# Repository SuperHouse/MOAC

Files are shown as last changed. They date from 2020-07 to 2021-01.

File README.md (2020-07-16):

Mini Open Adaptive Controller
==============================

Universal input device that allows external switches, buttons, etc
to be connected using 3.5mm mono plugs, and then emulate a USB
keyboard, mouse, joystick, or game controller to send HID events
to a computer or game console.

This allows custom-made assistive-technology input devices to be
connected to a computer or game console. Functionally this is very
similar to the Microsoft Xbox Adaptive Controller, but with fewer
inputs, a fully open-source design, a display, and more device emulation
options.

Based on the ATmega32u4 microcontroller, compatible with the Arduino
Leonardo.

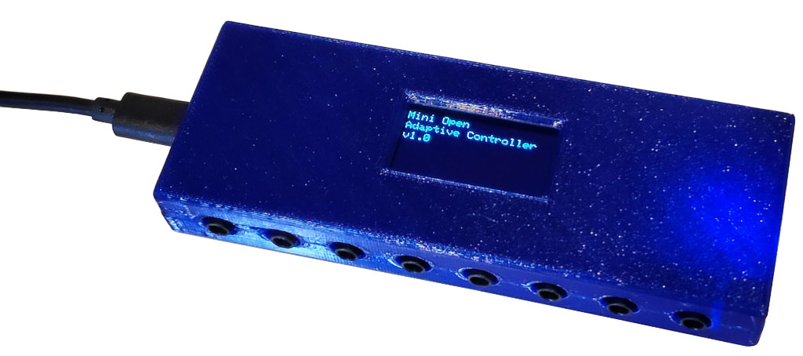
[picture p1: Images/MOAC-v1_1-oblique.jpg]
Mini Open Adaptive Controller


Features:

 * 8 switch inputs with 3.5mm mono sockets
 * USB-C socket for connection to computer, game controller, etc
 * Customise the software to suit your needs
 * 128x64 OLED module (SH1106)
 * ATmega 32u4 MCU (Arduino compatible)
 * Piezo beeper
 * Beep on/off switch
 * HWB (hardware boot) button and solder jumper to allow disabling bootloader

You can view more details at:

  http://www.superhouse.tv/moac

Hardware
--------
The "Hardware" directory contains the PCB design as an EAGLE project.
EAGLE PCB design software is available from Autodesk free for
non-commercial use.

Firmware
--------
The "Firmware" directory contains multiple versions. We have experimented
with different OLEDs and libraries during development, so this is a
collection of the different firmware versions.

The most recent hardware uses a 128x64 OLED with the SH1106 driver.

Unfortunately the various SH1106 drivers are a bit strange, and the best
I've found is the version of Adafruit's SSD1306 library that was forked
by wonho-maker and modified to add SSD1306 support. That version is not
available through the Arduino library manager, so it's been embedded
directly within the project.

Enclosure
---------
The "Enclosure" directory contains STLs for a case that can be
3D-printed.

The two halves of the case should be printed with the flat face down to
the printer bed.

The case can be held shut by countersunk self-tapping screws.

Credits
-------
 * Jonathan Oxer <jon@oxer.com.au>
 * Chris Fryer <chris.fryer78@gmail.com>

License
-------
Copyright 2018-2020 SuperHouse Automation Pty Ltd  www.superhouse.tv  

The hardware portion of this project is licensed under the TAPR Open
Hardware License (www.tapr.org/OHL). The "license" folder within this
repository contains a copy of this license in plain text format.

The software portion of this project is licensed under the Simplified
BSD License. The "licence" folder within this project contains a
copy of this license in plain text format.

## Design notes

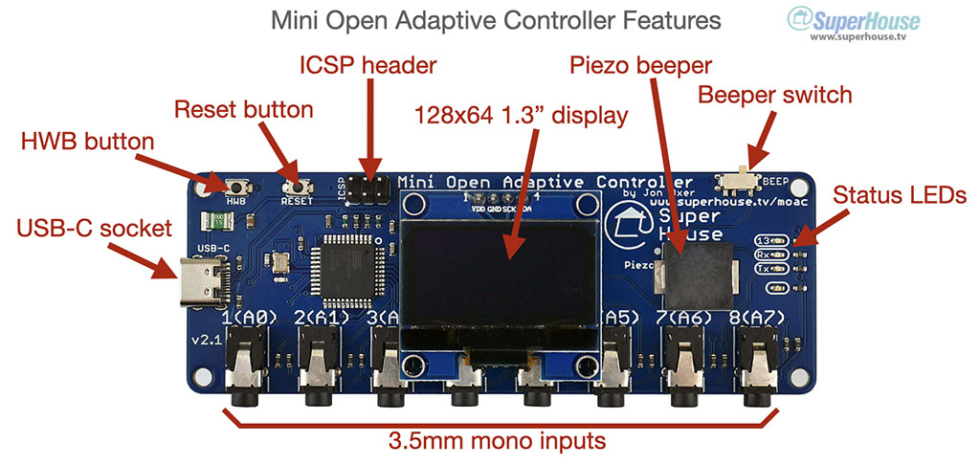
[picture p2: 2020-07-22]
Images/MOAC-v2_1-features.jpg

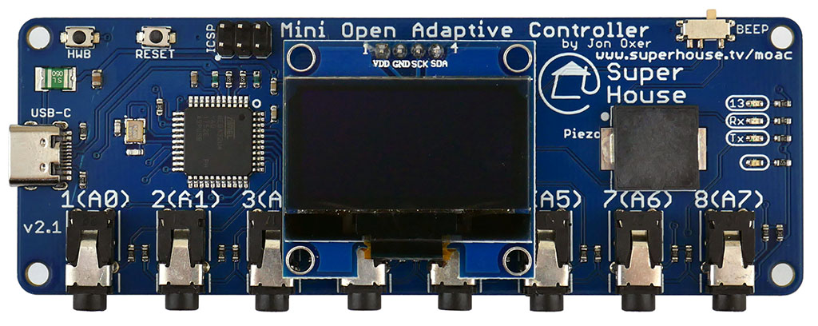
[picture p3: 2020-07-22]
Images/MOAC-v2_1-top.jpg

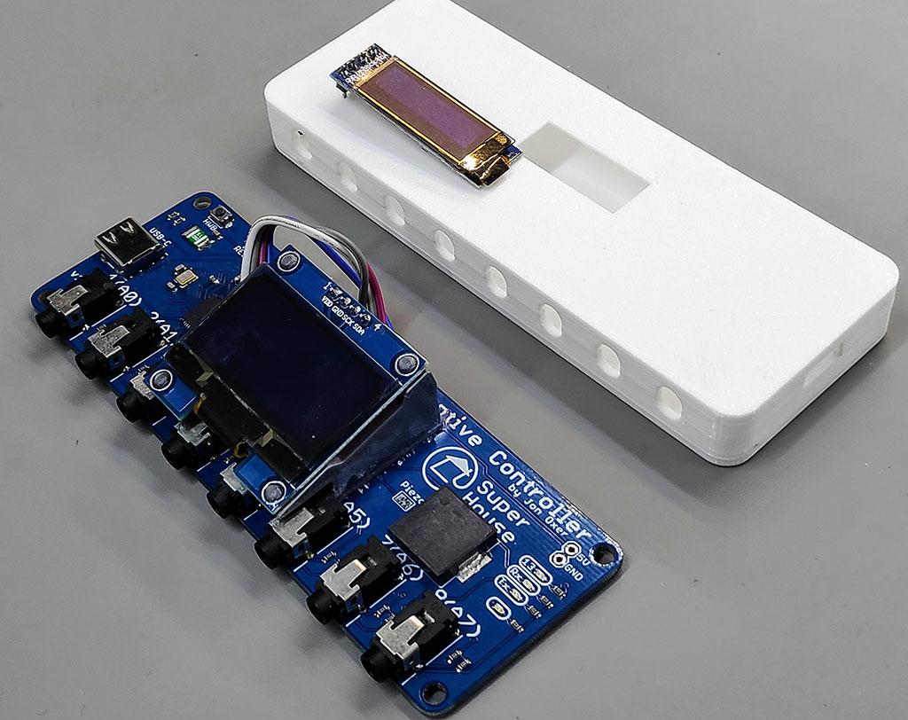
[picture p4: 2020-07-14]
Images/MOAC-v1_0-screen-size.jpg

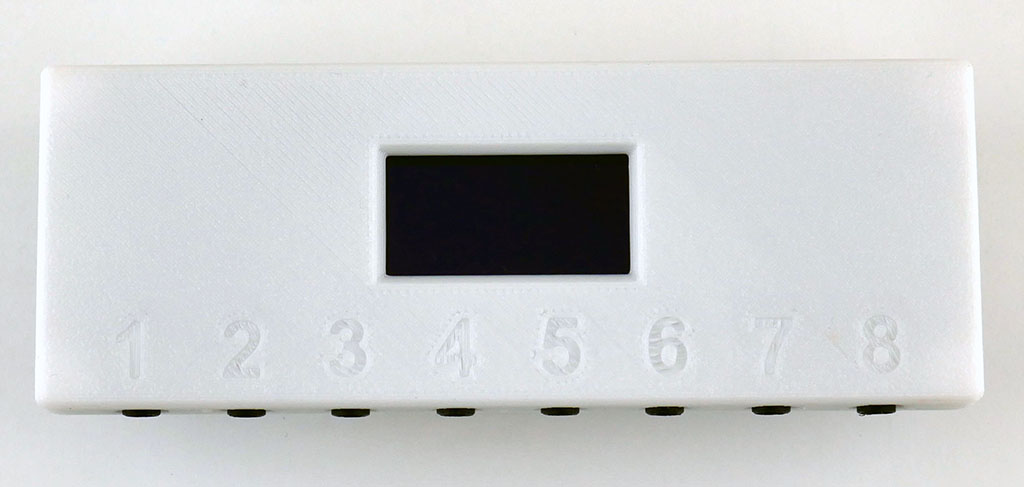
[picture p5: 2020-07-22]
Images/MOAC-v2_1-case-front.jpg

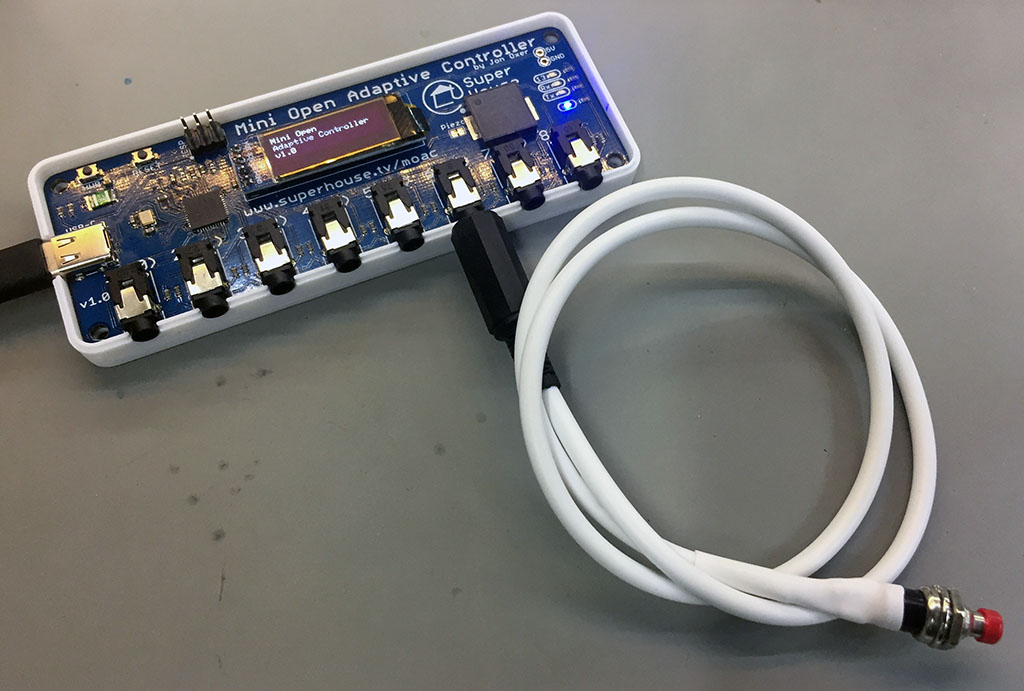
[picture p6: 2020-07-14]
Images/MOAC-v1_0-prototype-1-raw.jpg

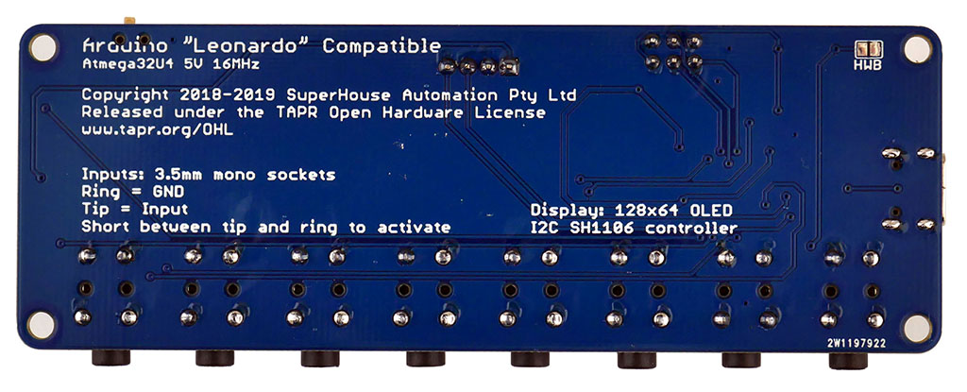
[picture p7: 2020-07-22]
Images/MOAC-v2_1-bottom.jpg

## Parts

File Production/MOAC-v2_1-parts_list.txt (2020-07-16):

Partlist

Exported from MOAC.sch at 16/7/20 12:54 PM

EAGLE Version 9.6.2 Copyright (c) 1988-2020 Autodesk, Inc.

Assembly variant: 

Part     Value                   Device                  Package              Library                 Sheet

C1       100nF                   CAP0603                 C0603                SuperHouse-DiscreteSemi 1
C2       100nF                   CAP0603                 C0603                SuperHouse-DiscreteSemi 1
C3       10uF                    CAP0805                 C0805                SuperHouse-DiscreteSemi 1
C4       1uF                     CAP0603                 C0603                SuperHouse-DiscreteSemi 1
C5       15pF                    CAP0603                 C0603                SuperHouse-DiscreteSemi 1
C6       15pF                    CAP0603                 C0603                SuperHouse-DiscreteSemi 1
F1       500mA PTC 1812          PTC050                  1812                 SuperHouse-Fuses        1
IC1      ATMEGA32U4NT-TQFP       ATMEGA32U4NT-TQFP       TQFP44               SuperHouse-MCUs         1
ICSP     ICSP                    ICSPPTH                 2X03PTH              SuperHouse-Connectors   1
J1       3.5mm                   AUDIO-JACK-PJ321        AUDIO-JACK-PJ321     SuperHouse-Connectors   1
J2       3.5mm                   AUDIO-JACK-PJ321        AUDIO-JACK-PJ321     SuperHouse-Connectors   1
J3       3.5mm                   AUDIO-JACK-PJ321        AUDIO-JACK-PJ321     SuperHouse-Connectors   1
J4       3.5mm                   AUDIO-JACK-PJ321        AUDIO-JACK-PJ321     SuperHouse-Connectors   1
J5       3.5mm                   AUDIO-JACK-PJ321        AUDIO-JACK-PJ321     SuperHouse-Connectors   1
J6       3.5mm                   AUDIO-JACK-PJ321        AUDIO-JACK-PJ321     SuperHouse-Connectors   1
J7       3.5mm                   AUDIO-JACK-PJ321        AUDIO-JACK-PJ321     SuperHouse-Connectors   1
J8       3.5mm                   AUDIO-JACK-PJ321        AUDIO-JACK-PJ321     SuperHouse-Connectors   1
J10      USB-C-16P-16P           USB-C-16P-16P           USB-C-16P            SuperHouse-Connectors   1
LED1     BLUE                    LED0603                 LED-0603             SuperHouse-LEDs         1
LED2     RED                     LED0603                 LED-0603             SuperHouse-LEDs         1
LED3     GREEN                   LED0603                 LED-0603             SuperHouse-LEDs         1
LED4     RED                     LED0603                 LED-0603             SuperHouse-LEDs         1
MOD2     OLED-I2C128X64-1.3-5.08 OLED-I2C128X64-1.3-5.08 OLED-128X64-1.3-5.08 SuperHouse-Displays     1
PIEZO    BUZZERSMD12X12          BUZZERSMD12X12          BUZZER-12X12-SMT     SuperHouse-Audio        1
R1       22R                     RESISTOR0603            R0603                SuperHouse-DiscreteSemi 1
R2       10K                     RESISTOR0603            R0603                SuperHouse-DiscreteSemi 1
R3       4K7                     RESISTOR0603            R0603                SuperHouse-DiscreteSemi 1
R4       1K                      RESISTOR0603            R0603                SuperHouse-DiscreteSemi 1
R5       1K                      RESISTOR0603            R0603                SuperHouse-DiscreteSemi 1
R6       22R                     RESISTOR0603            R0603                SuperHouse-DiscreteSemi 1
R7       5.1K                    RESISTOR0603            R0603                SuperHouse-DiscreteSemi 1
R8       1K                      RESISTOR0603            R0603                SuperHouse-DiscreteSemi 1
R9       1K                      RESISTOR0603            R0603                SuperHouse-DiscreteSemi 1
R10      1K                      RESISTOR0603            R0603                SuperHouse-DiscreteSemi 1
R11      1K                      RESISTOR0603            R0603                SuperHouse-DiscreteSemi 1
R12      1K                      RESISTOR0603            R0603                SuperHouse-DiscreteSemi 1
R13      10K                     RESISTOR0603            R0603                SuperHouse-DiscreteSemi 1
R14      10K                     RESISTOR0603            R0603                SuperHouse-DiscreteSemi 1
R15      10K                     RESISTOR0603            R0603                SuperHouse-DiscreteSemi 1
R16      10K                     RESISTOR0603            R0603                SuperHouse-DiscreteSemi 1
R17      1K                      RESISTOR0603            R0603                SuperHouse-DiscreteSemi 1
R18      5.1K                    RESISTOR0603            R0603                SuperHouse-DiscreteSemi 1
R19      1K                      RESISTOR0603            R0603                SuperHouse-DiscreteSemi 1
R20      1K                      RESISTOR0603            R0603                SuperHouse-DiscreteSemi 1
R21      1K                      RESISTOR0603            R0603                SuperHouse-DiscreteSemi 1
R22      10K                     RESISTOR0603            R0603                SuperHouse-DiscreteSemi 1
R23      10K                     RESISTOR0603            R0603                SuperHouse-DiscreteSemi 1
R24      10K                     RESISTOR0603            R0603                SuperHouse-DiscreteSemi 1
R25      10K                     RESISTOR0603            R0603                SuperHouse-DiscreteSemi 1
S9       RESET                   TAC_SWITCH_2PINSMT      TACTILE_SMD_3X4X2    SuperHouse-Switches     1
S10      HWB                     TAC_SWITCH_2PINSMT      TACTILE_SMD_3X4X2    SuperHouse-Switches     1
SJ1      HWB                     SJ-NORMAL               SJ                   SuperHouse-Jumpers      1
SW1      SWITCH-SPDT-4TABSSMT    SWITCH-SPDT-4TABSSMT    MK-12C02             SuperHouse-Switches     1
XTL1     16MHz                   CRYSTAL-GND3X2          CRYSTAL-SMD-3X2      SuperHouse-Oscillators  1
Z1       PGB1010603              TVS0603                 TVS0603              SuperHouse-DiscreteSemi 1
Z2       PGB1010603              TVS0603                 TVS0603              SuperHouse-DiscreteSemi 1

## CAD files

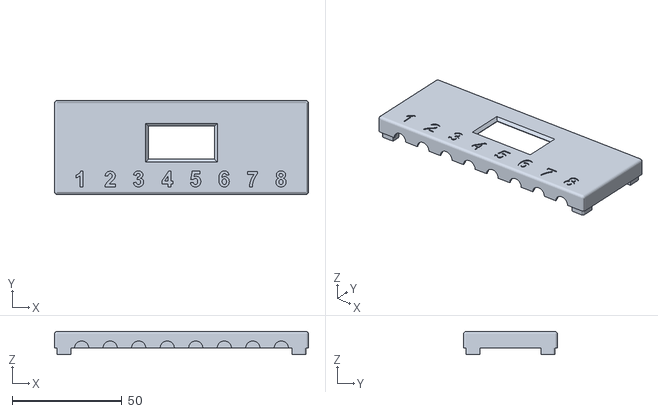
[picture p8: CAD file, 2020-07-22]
Enclosure/MOAC-case-top-v17.stl
115.8 x 42.8 x 10.6

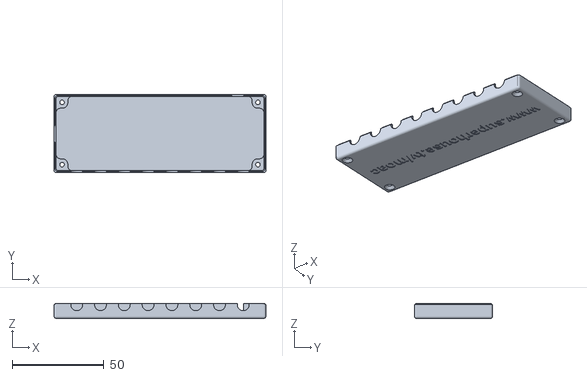
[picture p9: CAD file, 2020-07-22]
Enclosure/MOAC-case-bottom-v17.stl
115.8 x 42.8 x 8.10

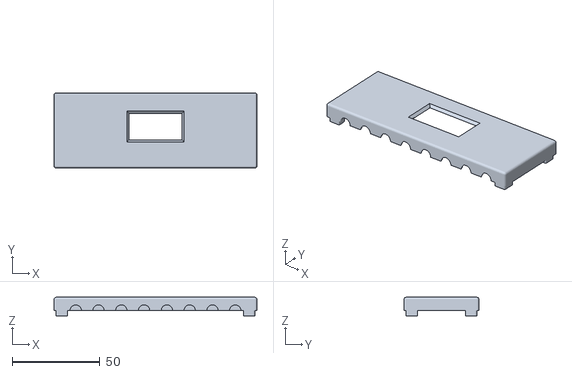
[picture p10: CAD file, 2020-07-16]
Enclosure/MOAC-case-top-v14.stl
115.8 x 42.8 x 10.6

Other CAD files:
Production/MOAC-tcream-v2_1.dxf
Enclosure/MOAC-case-top-v16.stl
Enclosure/MOAC-case-bottom-v16.stl
Enclosure/MOAC-case-bottom-v14.stl

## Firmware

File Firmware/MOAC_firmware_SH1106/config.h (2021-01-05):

/* ----------------- General config -------------------------------- */
// Messages generated by the inputs
char *g_macro_messages[] = {
  "a",       // 1: letter "a"
  "b\n",     // 2: letter "b" then start a new line
  "Hi ",     // 3: word "Hi" then a space
  "there\n", // 4: word "there" then start a new line
  "5",       // 5: number "5"
  "6",       // 6: number "6"
  "warp",    // Special "mouse warp" command
  "For more info, see: https://www.superhouse.tv/moac \n"  // 8: Print a help message!
};

// Mouse warp locations. Any input can be defined as a "warp" button, which
// will cause the mouse cursor to jump to each of the coordinates in turn.
// Warp locations are X/Y values, starting at 0,0 in the top left corner of
// the screen and ending at 1000,1000 in the bottom right corner of the screen.
// Center of the screen is 500,500.
uint16_t warp_locations[][2] = { {250,250}, {500,250}, {500,500}, {750,750}, {980,980}, {10,970} };

/* Audible feedback */
#define ENABLE_BEEP      true            // Can also be controlled by a switch
#define BEEP_DURATION       2            // 100 Milliseconds
#define BEEP_TONE        2000            // Frequency in Hz

/* OLED display */
#define DISPLAY_TIMEOUT     5            // Seconds

/* ----------------- Hardware-specific config ---------------------- */
/* Button inputs */
uint8_t g_input_pin_list[8] = { A0, A1, A2, A3, A4, A5, A6, A7 };

/* Piezo buzzer */
#define PIEZO_PIN          11            // Audible output

/* OLED display */
#define OLED_RESET         -1            // No dedicated reset connection

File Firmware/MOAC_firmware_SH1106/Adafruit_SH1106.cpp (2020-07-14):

/*********************************************************************
This is a library for our Monochrome OLEDs based on SSD1306 drivers

  Pick one up today in the adafruit shop!
  ------> http://www.adafruit.com/category/63_98

These displays use SPI to communicate, 4 or 5 pins are required to  
interface

Adafruit invests time and resources providing this open source code, 
please support Adafruit and open-source hardware by purchasing 
products from Adafruit!

Written by Limor Fried/Ladyada  for Adafruit Industries.  
BSD license, check license.txt for more information
All text above, and the splash screen below must be included in any redistribution
*********************************************************************/

/*********************************************************************
I change the adafruit SSD1306 to SH1106

SH1106 driver similar to SSD1306 so, just change the display() method.

However, SH1106 driver don't provide several functions such as scroll commands.


*********************************************************************/

#include <avr/pgmspace.h>
#ifndef __SAM3X8E__
 #include <util/delay.h>
#endif
#include <stdlib.h>

#include <Wire.h>

#include "Adafruit_GFX.h"
#include "Adafruit_SH1106.h"

// the memory buffer for the LCD

static uint8_t buffer[SH1106_LCDHEIGHT * SH1106_LCDWIDTH / 8] = { 
0x00, 0x00, 0x00, 0x00, 0x00, 0x00, 0x00, 0x00, 0x00, 0x00, 0x00, 0x00, 0x00, 0x00, 0x00, 0x00,
0x00, 0x00, 0x00, 0x00, 0x00, 0x00, 0x00, 0x00, 0x00, 0x00, 0x00, 0x00, 0x00, 0x00, 0x00, 0x00,
0x00, 0x00, 0x00, 0x00, 0x00, 0x00, 0x00, 0x00, 0x00, 0x00, 0x00, 0x00, 0x00, 0x00, 0x00, 0x00,
0x00, 0x00, 0x00, 0x00, 0x00, 0x00, 0x00, 0x00, 0x00, 0x00, 0x00, 0x00, 0x00, 0x00, 0x00, 0x80,
0x80, 0x80, 0x00, 0x00, 0x00, 0x00, 0x00, 0x00, 0x00, 0x00, 0x00, 0x00, 0x00, 0x00, 0x00, 0x00,
0x00, 0x80, 0x80, 0xC0, 0xC0, 0x00, 0x00, 0x00, 0x00, 0x00, 0x00, 0x00, 0x00, 0x00, 0x00, 0x00,
0x00, 0x00, 0x00, 0x00, 0x00, 0x00, 0x00, 0x00, 0x00, 0x00, 0x00, 0x00, 0x00, 0x00, 0x00, 0x00,
0x00, 0x00, 0x00, 0x00, 0x00, 0x00, 0x00, 0x00, 0x00, 0x00, 0x00, 0x00, 0x00, 0x00, 0x00, 0x00,
0x00, 0x00, 0x00, 0x00, 0x00, 0x00, 0x00, 0x00, 0x00, 0x00, 0x00, 0x00, 0x00, 0x00, 0x00, 0x00,
0x00, 0x00, 0x00, 0x00, 0x80, 0xC0, 0xE0, 0xF0, 0xF8, 0xFC, 0xF8, 0xE0, 0x00, 0x00, 0x00, 0x00,
0x00, 0x00, 0x00, 0x00, 0x00, 0x00, 0x00, 0x00, 0x00, 0x00, 0x00, 0x00, 0x00, 0x80, 0x80, 0x80,
0x80, 0x80, 0x00, 0x80, 0x80, 0x00, 0x00, 0x00, 0x00, 0x80, 0x80, 0x80, 0x80, 0x80, 0x00, 0xFF,
#if (SH1106_LCDHEIGHT * SH1106_LCDWIDTH > 96*16)
0xFF, 0xFF, 0x00, 0x00, 0x00, 0x00, 0x80, 0x80, 0x80, 0x80, 0x00, 0x00, 0x80, 0x80, 0x00, 0x00,
0x80, 0xFF, 0xFF, 0x80, 0x80, 0x00, 0x80, 0x80, 0x00, 0x80, 0x80, 0x80, 0x80, 0x00, 0x80, 0x80,
0x00, 0x00, 0x00, 0x00, 0x00, 0x80, 0x80, 0x00, 0x00, 0x8C, 0x8E, 0x84, 0x00, 0x00, 0x80, 0xF8,
0xF8, 0xF8, 0x80, 0x00, 0x00, 0x00, 0x00, 0x00, 0x00, 0x00, 0x00, 0x00, 0x00, 0x00, 0x00, 0x00,
0xF0, 0xF0, 0xF0, 0xF0, 0xF0, 0xF0, 0xF0, 0xF0, 0xF0, 0xF0, 0xF0, 0xF0, 0xE0, 0xE0, 0xC0, 0x80,
0x00, 0xE0, 0xFC, 0xFE, 0xFF, 0xFF, 0xFF, 0x7F, 0xFF, 0xFF, 0xFF, 0xFF, 0xFF, 0x00, 0x00, 0x00,
0x00, 0x00, 0x00, 0x00, 0x00, 0x00, 0x00, 0x00, 0x00, 0x00, 0x00, 0xFE, 0xFF, 0xC7, 0x01, 0x01,
0x01, 0x01, 0x83, 0xFF, 0xFF, 0x00, 0x00, 0x7C, 0xFE, 0xC7, 0x01, 0x01, 0x01, 0x01, 0x83, 0xFF,
0xFF, 0xFF, 0x00, 0x38, 0xFE, 0xC7, 0x83, 0x01, 0x01, 0x01, 0x83, 0xC7, 0xFF, 0xFF, 0x00, 0x00,
0x01, 0xFF, 0xFF, 0x01, 0x01, 0x00, 0xFF, 0xFF, 0x07, 0x01, 0x01, 0x01, 0x00, 0x00, 0x7F, 0xFF,
0x80, 0x00, 0x00, 0x00, 0xFF, 0xFF, 0x7F, 0x00, 0x00, 0xFF, 0xFF, 0xFF, 0x00, 0x00, 0x01, 0xFF,
0xFF, 0xFF, 0x01, 0x00, 0x00, 0x00, 0x00, 0x00, 0x00, 0x00, 0x00, 0x00, 0x00, 0x00, 0x00, 0x00,
0x03, 0x0F, 0x3F, 0x7F, 0x7F, 0xFF, 0xFF, 0xFF, 0xFF, 0xFF, 0xFF, 0xFF, 0xE7, 0xC7, 0xC7, 0x8F,
0x8F, 0x9F, 0xBF, 0xFF, 0xFF, 0xC3, 0xC0, 0xF0, 0xFF, 0xFF, 0xFF, 0xFF, 0xFF, 0xFC, 0xFC, 0xFC,
0xFC, 0xFC, 0xFC, 0xFC, 0xFC, 0xF8, 0xF8, 0xF0, 0xF0, 0xE0, 0xC0, 0x00, 0x01, 0x03, 0x03, 0x03,
0x03, 0x03, 0x01, 0x03, 0x03, 0x00, 0x00, 0x00, 0x00, 0x01, 0x03, 0x03, 0x03, 0x03, 0x01, 0x01,
0x03, 0x01, 0x00, 0x00, 0x00, 0x01, 0x03, 0x03, 0x03, 0x03, 0x01, 0x01, 0x03, 0x03, 0x00, 0x00,
0x00, 0x03, 0x03, 0x00, 0x00, 0x00, 0x03, 0x03, 0x00, 0x00, 0x00, 0x00, 0x00, 0x00, 0x00, 0x01,
0x03, 0x03, 0x03, 0x03, 0x03, 0x01, 0x00, 0x00, 0x00, 0x01, 0x03, 0x01, 0x00, 0x00, 0x00, 0x03,
0x03, 0x01, 0x00, 0x00, 0x00, 0x00, 0x00, 0x00, 0x00, 0x00, 0x00, 0x00, 0x00, 0x00, 0x00, 0x00,
#if (SH1106_LCDHEIGHT == 64)
0x00, 0x00, 0x00, 0x80, 0xC0, 0xE0, 0xF0, 0xF9, 0xFF, 0xFF, 0xFF, 0xFF, 0xFF, 0x3F, 0x1F, 0x0F,
0x87, 0xC7, 0xF7, 0xFF, 0xFF, 0x1F, 0x1F, 0x3D, 0xFC, 0xF8, 0xF8, 0xF8, 0xF8, 0x7C, 0x7D, 0xFF,
0xFF, 0xFF, 0xFF, 0xFF, 0xFF, 0xFF, 0xFF, 0x7F, 0x3F, 0x0F, 0x07, 0x00, 0x30, 0x30, 0x00, 0x00,
0x00, 0x00, 0x00, 0x00, 0x00, 0x00, 0x00, 0x00, 0x00, 0x00, 0x00, 0x00, 0x00, 0x00, 0x00, 0x00,
0x00, 0x00, 0x00, 0x00, 0xFE, 0xFE, 0xFC, 0x00, 0x00, 0x00, 0x00, 0x00, 0x00, 0x00, 0x00, 0x00,
0x00, 0x00, 0x00, 0x00, 0x00, 0x00, 0x00, 0x00, 0x00, 0x00, 0x00, 0x00, 0x00, 0xE0, 0xC0, 0x00,
0x00, 0x00, 0x00, 0x00, 0x00, 0x00, 0x00, 0x00, 0x00, 0x00, 0x30, 0x30, 0x00, 0x00, 0x00, 0x00,
0x00, 0x00, 0x00, 0x00, 0x00, 0x00, 0x00, 0x00, 0x00, 0x00, 0x00, 0x00, 0x00, 0x00, 0x00, 0x00,
0x00, 0xC0, 0xFE, 0xFF, 0xFF, 0xFF, 0xFF, 0xFF, 0xFF, 0xFF, 0xFF, 0xFF, 0x7F, 0x7F, 0x3F, 0x1F,
0x0F, 0x07, 0x1F, 0x7F, 0xFF, 0xFF, 0xF8, 0xF8, 0xFF, 0xFF, 0xFF, 0xFF, 0xFF, 0xFE, 0xF8, 0xE0,
0x00, 0x00, 0x00, 0x01, 0x00, 0x00, 0x00, 0x00, 0x00, 0x00, 0x00, 0x00, 0xFE, 0xFE, 0x00, 0x00,
0x00, 0xFC, 0xFE, 0xFC, 0x0C, 0x06, 0x06, 0x0E, 0xFC, 0xF8, 0x00, 0x00, 0xF0, 0xF8, 0x1C, 0x0E,
0x06, 0x06, 0x06, 0x0C, 0xFF, 0xFF, 0xFF, 0x00, 0x00, 0xFE, 0xFE, 0x00, 0x00, 0x00, 0x00, 0xFC,
0xFE, 0xFC, 0x00, 0x18, 0x3C, 0x7E, 0x66, 0xE6, 0xCE, 0x84, 0x00, 0x00, 0x06, 0xFF, 0xFF, 0x06,
0x06, 0xFC, 0xFE, 0xFC, 0x0C, 0x06, 0x06, 0x06, 0x00, 0x00, 0xFE, 0xFE, 0x00, 0x00, 0xC0, 0xF8,
0xFC, 0x4E, 0x46, 0x46, 0x46, 0x4E, 0x7C, 0x78, 0x40, 0x18, 0x3C, 0x76, 0xE6, 0xCE, 0xCC, 0x80,
0x00, 0x00, 0x00, 0x00, 0x00, 0x00, 0x00, 0x00, 0x00, 0x00, 0x00, 0x00, 0x00, 0x00, 0x00, 0x00,
0x00, 0x00, 0x00, 0x00, 0x01, 0x07, 0x0F, 0x1F, 0x1F, 0x3F, 0x3F, 0x3F, 0x3F, 0x1F, 0x0F, 0x03,
0x00, 0x00, 0x00, 0x00, 0x00, 0x00, 0x00, 0x00, 0x00, 0x00, 0x00, 0x00, 0x0F, 0x0F, 0x00, 0x00,
0x00, 0x0F, 0x0F, 0x0F, 0x00, 0x00, 0x00, 0x00, 0x0F, 0x0F, 0x00, 0x00, 0x03, 0x07, 0x0E, 0x0C,
0x18, 0x18, 0x0C, 0x06, 0x0F, 0x0F, 0x0F, 0x00, 0x00, 0x01, 0x0F, 0x0E, 0x0C, 0x18, 0x0C, 0x0F,
0x07, 0x01, 0x00, 0x04, 0x0E, 0x0C, 0x18, 0x0C, 0x0F, 0x07, 0x00, 0x00, 0x00, 0x0F, 0x0F, 0x00,
0x00, 0x0F, 0x0F, 0x0F, 0x00, 0x00, 0x00, 0x00, 0x00, 0x00, 0x0F, 0x0F, 0x00, 0x00, 0x00, 0x07,
0x07, 0x0C, 0x0C, 0x18, 0x1C, 0x0C, 0x06, 0x06, 0x00, 0x04, 0x0E, 0x0C, 0x18, 0x0C, 0x0F, 0x07,
0x00, 0x00, 0x00, 0x00, 0x00, 0x00, 0x00, 0x00, 0x00, 0x00, 0x00, 0x00, 0x00, 0x00, 0x00, 0x00,
0x00, 0x00, 0x00, 0x00, 0x00, 0x00, 0x00, 0x00, 0x00, 0x00, 0x00, 0x00, 0x00, 0x00, 0x00, 0x00,
0x00, 0x00, 0x00, 0x00, 0x00, 0x00, 0x00, 0x00, 0x00, 0x00, 0x00, 0x00, 0x00, 0x00, 0x00, 0x00,
0x00, 0x00, 0x00, 0x00, 0x00, 0x00, 0x00, 0x00, 0x00, 0x00, 0x00, 0x00, 0x00, 0x00, 0x00, 0x00,
0x00, 0x00, 0x00, 0x00, 0x00, 0x00, 0x00, 0x00, 0x00, 0x00, 0x00, 0x00, 0x00, 0x00, 0x00, 0x00,
0x00, 0x00, 0x00, 0x00, 0x00, 0x00, 0x00, 0x00, 0x00, 0x00, 0x00, 0x00, 0x00, 0x00, 0x00, 0x00,
0x00, 0x00, 0x00, 0x00, 0x00, 0x00, 0x00, 0x00, 0x00, 0x00, 0x00, 0x00, 0x00, 0x00, 0x00, 0x00,
0x00, 0x00, 0x00, 0x00, 0x00, 0x00, 0x00, 0x00, 0x00, 0x00, 0x00, 0x00, 0x00, 0x00, 0x00, 0x00
#endif
#endif
};

#define sh1106_swap(a, b) { int16_t t = a; a = b; b = t; }

// the most basic function, set a single pixel
void Adafruit_SH1106::drawPixel(int16_t x, int16_t y, uint16_t color) {
  if ((x < 0) || (x >= width()) || (y < 0) || (y >= height()))
    return;

  // check rotation, move pixel around if necessary
  switch (getRotation()) {
  case 1:
    sh1106_swap(x, y);
    x = WIDTH - x - 1;
    break;
  case 2:
    x = WIDTH - x - 1;
    y = HEIGHT - y - 1;
    break;
  case 3:
    sh1106_swap(x, y);
    y = HEIGHT - y - 1;
    break;
  }  

  // x is which column
    switch (color) 
    {
      case WHITE:   buffer[x+ (y/8)*SH1106_LCDWIDTH] |=  (1 << (y&7)); break;
      case BLACK:   buffer[x+ (y/8)*SH1106_LCDWIDTH] &= ~(1 << (y&7)); break; 
      case INVERSE: buffer[x+ (y/8)*SH1106_LCDWIDTH] ^=  (1 << (y&7)); break; 
    }
    
}

Adafruit_SH1106::Adafruit_SH1106(int8_t SID, int8_t SCLK, int8_t DC, int8_t RST, int8_t CS) : Adafruit_GFX(SH1106_LCDWIDTH, SH1106_LCDHEIGHT) {
  cs = CS;
  rst = RST;
  dc = DC;
  sclk = SCLK;
  sid = SID;
  hwSPI = false;
}

// constructor for hardware SPI - we indicate DataCommand, ChipSelect, Reset 
Adafruit_SH1106::Adafruit_SH1106(int8_t DC, int8_t RST, int8_t CS) : Adafruit_GFX(SH1106_LCDWIDTH, SH1106_LCDHEIGHT) {
  dc = DC;
  rst = RST;
  cs = CS;
  hwSPI = true;
}

// initializer for I2C - we only indicate the reset pin!
Adafruit_SH1106::Adafruit_SH1106(int8_t reset) :
Adafruit_GFX(SH1106_LCDWIDTH, SH1106_LCDHEIGHT) {
  sclk = dc = cs = sid = -1;
  rst = reset;
}
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

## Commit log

2018-11-14 Initial project import for v1.0 release
    [MOAC.brd, MOAC.sch]
2018-11-24 Improved designators
    [MOAC.brd, MOAC.sch]
2019-07-07 Replaced parts using SuperHouse libraries to add 3D models
    [MOAC.brd, MOAC.sch]
2019-07-11 Replaced 128x32 OLED with 128x64, 1.3in for v2.0 release
    [MOAC.brd, MOAC.sch]
2019-07-18 Changed ATmega32U4 from QFN to TQFP to save Jon's sanity for v2.0 release
    [MOAC.brd, MOAC.sch]
2019-07-31 Changed button 8 from A11 to A7, to fix Jon's silly mistake from way back in v1.0
    [MOAC.brd, MOAC.sch]
2020-03-18 Changed display from 128x32 to 128x64
    [MOAC.brd, MOAC.sch]
2020-05-05 Added piezo switch; replaced USB-C socket for v2.1 release
    [MOAC.brd, MOAC.sch]
2020-05-12 Final tweaks and DRC for v2.1 release
    [MOAC.brd, MOAC.sch]
2020-05-12 Added stencil DXF for v2.1
    [MOAC-tcream-v2_1.dxf]
2020-07-14 Begin restructuring project to merge hardware and software into one repository
    [MOAC-tcream-v2_1.dxf, MOAC.brd, MOAC.sch]
2020-07-14 Added enclosure STLs
    [MOAC-bracket-2.stl, MOAC-bracket.stl, MOAC-case-bottom-v12.stl, MOAC-case-top-v12.stl]
2020-07-16 Added beep switch slot to case
    [MOAC-bracket-2.stl, MOAC-bracket.stl, MOAC-case-bottom-v12.stl, MOAC-case-bottom-v14.stl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]
2020-07-16 Added input labels and URL to enclosure
    [MOAC-case-bottom-v16.stl, MOAC-case-top-v16.stl]
2020-07-22 Added input numbers and URL to case
    [MOAC-case-bottom-v17.stl, MOAC-case-top-v17.stl]
